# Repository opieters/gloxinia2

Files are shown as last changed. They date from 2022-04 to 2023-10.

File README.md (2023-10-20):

# gloxinia2

This is the second version of [Gloxinia](https://github.com/opieters/gloxinia), a research-focussed measurement platform that is tailored for deployment in greenhouses. Its goals are simple interconnectivity, flexbibility and cost-effectiveness.

## Architecture

The general architecture from the inital version remained, but some boards are not separate noted in place of add-on components. At it's core, the system comprises of a set of communicating nodes. Three possible options are:
- dicio: a node with serial interconnectivity, such that the system can interface with a computer. This node also features storage (16GB). This node can also send commands to other nodes in case of errors or crashes.
- sylvatica: a node with eight 16-bit ADCs
- planalta: a node with four LIAs (advanced analogue sensors)

All nodes communicate over a CAN bus and dicio nodes also have UART connection for communication computers. Plugging in a USB-C cable in the right port should suffice to connect to the system. Make sure to only plug cables to matching interfaces, since the hardware can be damaged otherwise. The interfaces are detailed in the PCB design and the interface section below. 

Note that the CAN bus requires termination. No automatic termination is implemented, so the use needs to manually terminate the CAN lines!

Each board interface also has an I2C port (not that some of the ports share the same physical interface), and analogue ports and a One Wire port. One Wire is currently not supported in the software. 

## Interfacing

Each node consists of a stack of boards. The base board with the analogue and digital processing, a botton connectivity board to interconnect different nodes and an optional top interfacing board (only for sylvatica).

### Dicio

Base board: [IF1] [IF2] [IF3] [IF4]
IF board: [Serial/USB] [] [CAN] [CAN]

### Sylvatica

Top board: [IF4] [IF5] [IF6] [IF7]
Base board: [IF1] [IF2] [IF3] [IF4]
IF board: [] [] [CAN] [CAN]

### Planalta

Base board: [IF1] [IF2] [IF3] [IF4]
IF board: [] [] [CAN] [CAN]

Note that IF1-4 are not feature-identical, IF1 supports a faster LIA (when others disabled) than IF2, 3 and 4 resp. See software implementation for details. These interfaces to no feature a 1W port.

## Software

The software consists of several parts: the embedded C code, the C++ GUI and the Python readout script. 

The embedded code is in the `firmware` folder. A separate MPLAB X project is created per hardware board (dicio, planalta and sylvatica). The code is written in C and compiled with the XC16 compiler. The code is written in a modular fashion, such that it is easy to add new features. The code is documented in the source files. Common files are included in the `lib2` folder. 

A bootloader project was also created to update the devices over CAN and UART, but this was not tested and should not yet be used in production. The UART version was slightly tested and first results were promising.

The GUI code is written in C++ using the Qt framework. A recent version of Qt 6 is necessary to build the project. Qt Designer files are included with in the `gui_qt` folder to get started with this project. 

## Enclousure

A 3D printable enclosure design is included in the `enclosure` folder, along with the STL files. The design is made in OpenSCAD.

A radiation shield was also designed for the environemental sensors, which is included in the

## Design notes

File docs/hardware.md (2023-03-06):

# Internal PIN connector

connector left

1  GND PS
3  AN1 OW1
5  AN2 OW2
7  AN3 OW3
9  AN4 OW4
11
13
15

connector right
1  VBUS   VUSBC
3  V3V3   GND
5  SDA    SCL
7  SYNC   CC1
9  D+     D-
11 CAN_C1 CAN_C2
13 RX     TX
15 nCTS   nRTS

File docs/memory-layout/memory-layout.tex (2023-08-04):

\documentclass[tikz]{standalone}

\usetikzlibrary{positioning}

\begin{document}
\begin{tikzpicture}
\begin{scope}[every node/.style={text width=4cm,align=center}]
  \node[draw] (dicio) {dicio configuration};
  \node[draw,below=0cm of dicio] (nodeconfig) {node configuration};
  \node[draw,below=0cm of nodeconfig] (data) {sample data};
\end{scope}
  
  \draw (dicio.north west) node[anchor=east] {0x0};
  \draw (nodeconfig.north west) node[anchor=east] {0x20};
  \draw (data.north west) node[anchor=east] {0x470};
  
  \draw (dicio.south east) node[anchor=west] {0x19};
  \draw (nodeconfig.south east) node[anchor=west] {0x469};
  \draw (data.south east) node[anchor=west] {0x1dacbff};
\end{tikzpicture}

\begin{tikzpicture}
\begin{scope}[every node/.style={text width=4cm,align=center}]
  \node[draw] (info) {node $n$ general info};
  \node[draw,below=0cm of info] (if1) {interface 1};
  \node[draw,below=0cm of if1] (s1-1) {sensor 1};
  \node[draw,below=0cm of s1-1] (s1-2) {sensor 2};
  \node[draw,below=0cm of s1-2] (s1-3) {sensor 3};
  \node[draw,below=0cm of s1-3] (s1-4) {sensor 4};
  \node[draw,below=0cm of s1-4] (if2) {interface 2};
  \node[draw,below=0cm of if2] (s2-1) {sensor 1};
  \node[draw,below=0cm of s2-1] (s2-2) {sensor 2};
  \node[draw,below=0cm of s2-2] (s2-3) {sensor 3};
  \node[draw,below=0cm of s2-3] (s2-4) {sensor 4};
  \node[draw,below=0cm of s2-4] (if3) {interface 3};
  \node[draw,below=0cm of if3] (if3-dots) {$\cdots$};
  \node[draw,below=0cm of if3-dots] (if4) {interface 4};
  \node[draw,below=0cm of if4] (if4-dots) {$\cdots$};
  \node[draw,below=0cm of if4-dots] (if5) {interface 5/reserved};
  \node[draw,below=0cm of if5] (if5-dots) {$\cdots$};
  \node[draw,below=0cm of if5-dots] (if6) {interface 6/reserved};
  \node[draw,below=0cm of if6] (if6-dots) {$\cdots$};
  \node[draw,below=0cm of if6-dots] (if7) {interface 7/reserved};
  \node[draw,below=0cm of if7] (if7-dots) {$\cdots$};
  \node[draw,below=0cm of if7-dots] (if8) {interface 8/reserved};
  \node[draw,below=0cm of if8] (if8-dots) {$\cdots$};
\end{scope}
  
  \draw (info.north west) node[anchor=east] {offset$_n$ + 0x0};
  \foreach \x/\y in {1/1,2/10,3/19,4/28,5/37,6/46,7/55,8/64} {
    \draw (if\x.north west) node[anchor=east] {offset$_n$ + 0x\y};
  }
  \foreach \x/\y in {1/9,2/0} {
    \draw (s\x-4.south east) node[anchor=west] {offset$_n$ + 0x\y};
  }
  \foreach \x/\y in {3/0,4/0,5/0,6/0,7/0,8/0} {
    \draw (if\x-dots.south east) node[anchor=west] {offset$_n$ + 0x\y};
  }
  
\end{tikzpicture}
\end{document}

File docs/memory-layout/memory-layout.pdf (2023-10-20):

dicio configuration

node configuration

sample data

0x0

0x20

0x470

0x19

0x469

0x1dacbff

node n general info

interface 1
sensor 1
sensor 2
sensor 3
sensor 4
interface 2
sensor 1
sensor 2
sensor 3
sensor 4
interface 3
- · ·
interface 4
- · ·
interface 5/reserved
- · ·
interface 6/reserved
- · ·
interface 7/reserved
- · ·
interface 8/reserved
- · ·

offsetn + 0x0

offsetn + 0x1

offsetn + 0x10

offsetn + 0x19

offsetn + 0x28

offsetn + 0x37

offsetn + 0x46

offsetn + 0x55

offsetn + 0x64

offsetn + 0x9

offsetn + 0x0

offsetn + 0x0

offsetn + 0x0

offsetn + 0x0

offsetn + 0x0

offsetn + 0x0

offsetn + 0x0

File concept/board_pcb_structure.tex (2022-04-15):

\documentclass[margin=2mm]{standalone}

\usepackage{tikz}
\usetikzlibrary{positioning,calc}

\begin{document}
\begin{tikzpicture}
    \draw[thick] (0,0) rectangle ++(10,10);

    \fill[green] (1,1) rectangle ++(8,8);

    \fill[red] (0.5,0) rectangle ++(9,2.5);
    \fill[gray] (0,4) rectangle ++(1.5,2);
    \fill[gray] (10,4) rectangle ++(-1.5,2);

    \foreach \x in {0,1,2,3,4} {
        \draw[ultra thick,blue] (1.75*\x+1,0) -- ++(1,0);
    }
    \draw[ultra thick,blue] (0,4.5) -- ++(0,1);
    \draw[ultra thick,blue] (10,4.5) -- ++(0,1);

\end{tikzpicture}
\end{document}

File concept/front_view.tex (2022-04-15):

\documentclass[margin=2mm]{standalone}

\usepackage{tikz}
\usetikzlibrary{positioning,calc}

\begin{document}
\begin{tikzpicture}
    \draw[thick] (0,0) rectangle ++(10,4);

    \foreach \x in {0,1,2,3,4} {
        \draw[ultra thick,blue] (1.75*\x+1,1) -- ++(1,0);
    }
    \foreach \x in {0,1,2,3,4} {
        \draw[ultra thick,blue] (1.75*\x+1,3) -- ++(1,0);
    }

    \fill[blue] (0,2) circle(2pt);
    \fill[blue] (10,2) circle(2pt);

\end{tikzpicture}
\end{document}

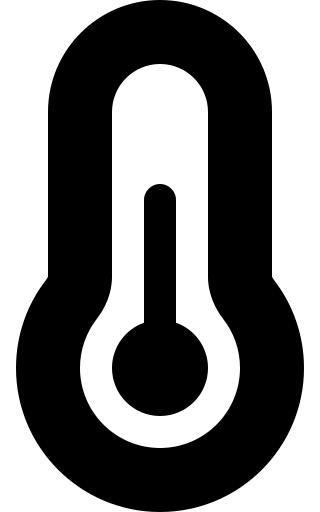
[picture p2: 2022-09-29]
gui_qt/GloxiniaConfigurator/images/temperature-rh-sensor.png

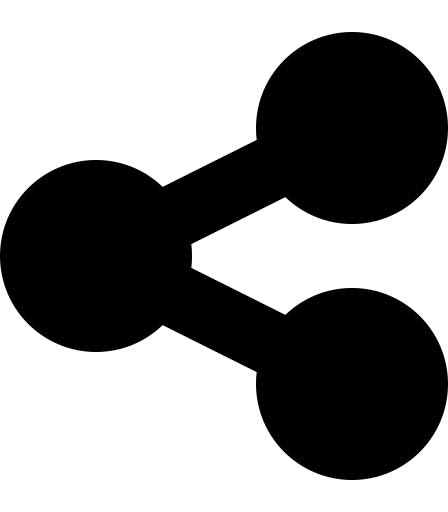
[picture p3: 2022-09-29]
gui_qt/GloxiniaConfigurator/images/node.png

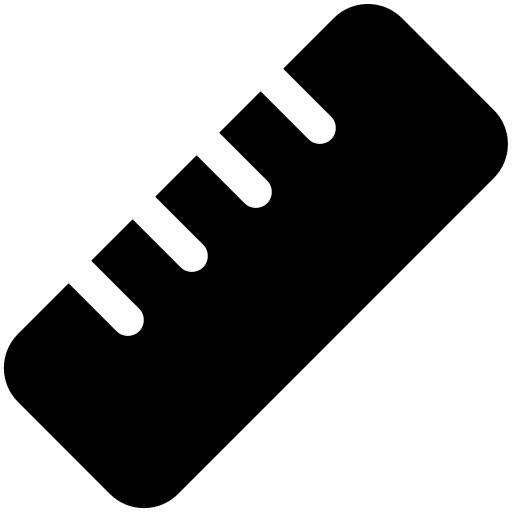
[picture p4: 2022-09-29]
gui_qt/GloxiniaConfigurator/images/general-sensor.png

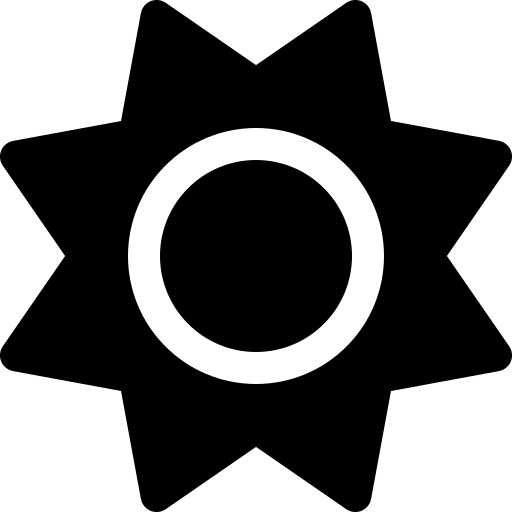
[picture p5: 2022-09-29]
gui_qt/GloxiniaConfigurator/images/light-sensor.png

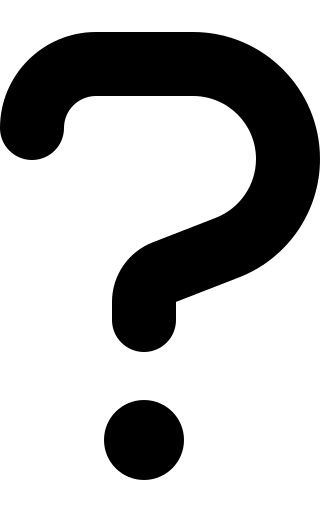
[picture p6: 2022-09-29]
gui_qt/GloxiniaConfigurator/images/unknown-sensor.png

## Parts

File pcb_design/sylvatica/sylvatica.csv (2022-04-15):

Source: | /home/opieters/PhD/gloxinia/board/sylvatica/sylvatica.sch
Date: | Tue 16 Jul 2019 10:46:27 CEST
Tool: | Eeschema 5.0.2-bee76a0~70~ubuntu18.04.1
Generator: | /home/opieters/PhD/gloxinia/board/bom-order.py
Component Count: | 106
Ref | Qnty | Value | Cmp name | Ref. Mouser | Ref. Farnell | Price
C9, | 1 | 1uF | C | 77-VJ0603A102GXJPBC
C10, | 1 | 0.01uF | C | 77-VJ0603A102GXJPBC
C11, C35, C36, C39, | 4 | C | C
C12, | 1 | 2.2uF | C | 77-VJ0603A102GXJPBC
C16, C14, C21, C19, C15, C45, C23, C24, C32, C34, C33, C37, C38, C31, C1, C2, C4, C6, C5, C7, C8, C3, | 22 | 0.1uF | C | 710-885012206071
C17, | 1 | 22uF | C | 963-TMK316BBJ226ML-T
C18, | 1 | 1uF | C | 963-TMK325B7105KD-T
C20, C13, C42, C44, | 4 | 10uF | C | 963-TMK325BJ106KM-P
C22, | 1 | 0.01uF | C | 81-GRM033C81E103KE4E
C41, C40, C26, C25, C28, C27, C30, C29, | 8 | 22nF | C | 80-C0603C223K3R
C46, C47, | 2 | 10pF | C | 603-CC603FRNPO9BN100
D1, D2, | 2 | LED | LED | 78-TLMS1000
H1, H3, H2, H4, | 4 | MountingHole | MountingHole
I0, I1, I2, I3, I4, I5, I6, I7, | 8 | AudioJack3 | AudioJack3 | 490-SJ1-3533NG
J1, | 1 | GloxiniaConnector | GloxiniaConnector
J9, | 1 | Conn_01x06_Female | Conn_01x06_Female
J14, | 1 | Conn_02x02_Odd_Even | Conn_02x02_Odd_Even
JA0, JA1, | 2 | Conn_01x03_Female | Conn_01x03_Female
JP1, | 1 | Jumper | Jumper
Q2, Q1, | 2 | Q_NMOS_GSD | Q_NMOS_GSD | 512-BSS138
R12, R14, | 2 | 0.22R | R | 667-ERJ-3RQFR22V
R13, | 1 | 1k | R | 652-CR0603-FX1001HLF
R15, R16, R9, R10, R19, | 5 | 10k | R | 284-APC0603B10K0N
R17, R18, | 2 | 750 | R | 603-RC0603FR-07750RL
R34, R33, R2, R1, R4, R3, R6, R5, | 8 | 20 | R | 71-CRCW060320R0FKEAC
R36, | 1 | 270 | R | 603-RC0603FR-07270RL
R37, | 1 | 1M | R | 603-RC0603FR-101ML
SW1, | 1 | SW_Push | SW_Push | 611-KMR621NGLFS
U5, U6, U8, U7, U1, U2, U4, U3, | 8 | PGA113 | PGA113 | 595-PGA113AIDGSR
U9, | 1 | ADS8332 | ADS8332 | 595-ADS8332IBPWR
U10, | 1 | dsPIC33EP512MC806 | dsPIC33EP512MC806 | 579-33EP512MC806IPT |  | 5
U11, | 1 | DG2034E | DG2034E | 78-DG2034EDQ-T1-GE3
U12, | 1 | LP2985-5.0 | LP2985-5.0
U13, | 1 | REF2033 | REF2033 | 595-REF2033AIDDCR
U14, | 1 | OPA320 | OPA320 | 595-OPA320AIDBVR
U15, U16, | 2 | SiP32431 | SiP32431
Y1, | 1 | Crystal_GND24 | Crystal_GND24 | 520-80-10-30B-CWNT
Total cost: | 5.00

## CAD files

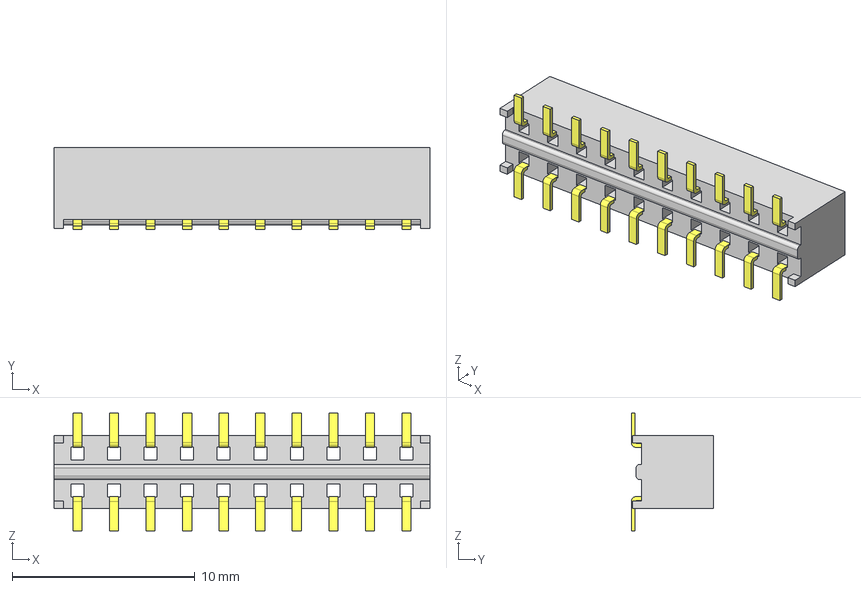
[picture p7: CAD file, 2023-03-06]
pcb_design/samtec/MMS-110-02-F-DV.stp
20.5 x 4.50 x 6.44 mm
C-63-02-10-DV
MMS-110-02-DV_socket

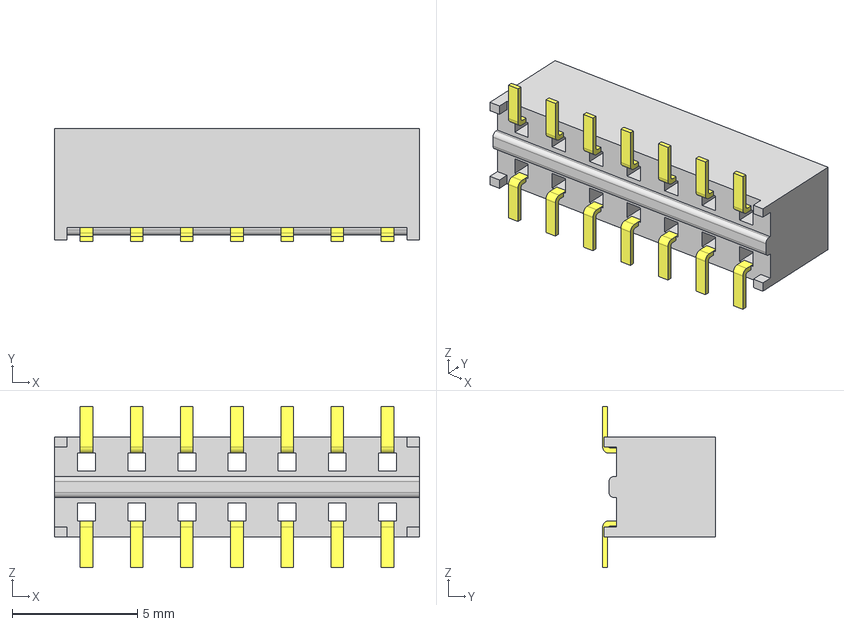
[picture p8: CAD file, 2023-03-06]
pcb_design/samtec/MMS-107-02-F-DV.stp
14.6 x 4.50 x 6.44 mm
C-63-02-07-DV
MMS-107-02-DV_socket

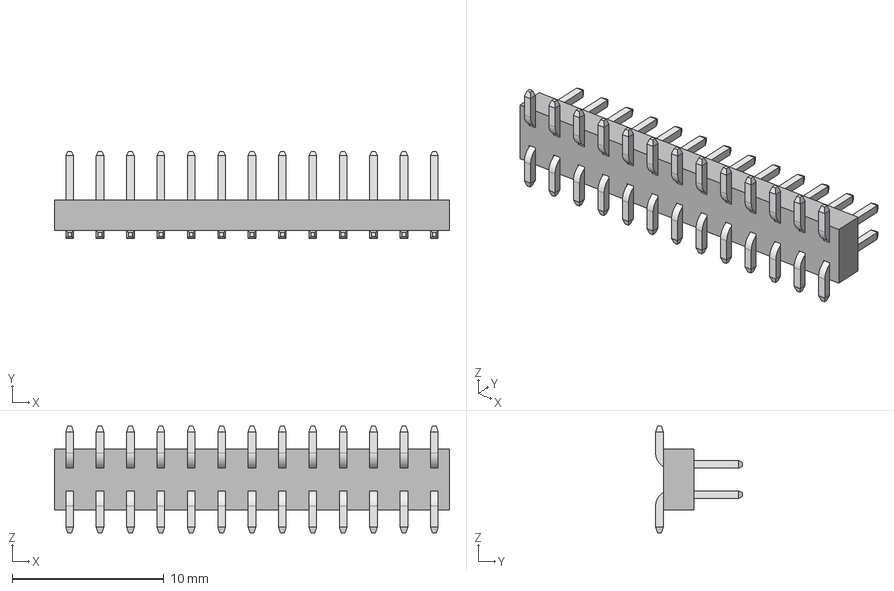
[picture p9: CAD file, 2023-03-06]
pcb_design/samtec/TMMH-113-01-T-DV.stp
26.0 x 5.71 x 7.04 mm
TMMH-113-01-T-DV-sm_pins2
TMMH-113-01-T-DV_pins1
TMMH-113-01-T-DV_body

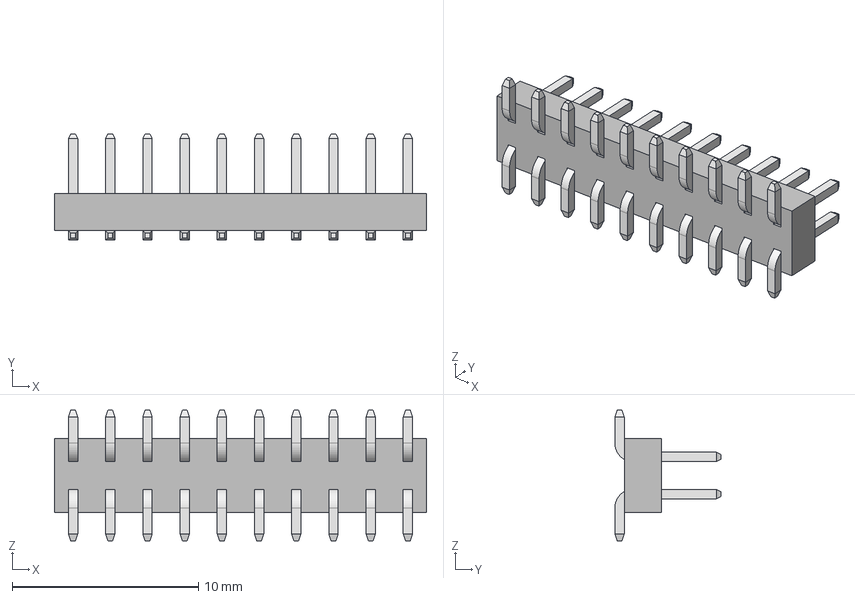
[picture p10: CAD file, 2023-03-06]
pcb_design/samtec/TMMH-110-01-T-DV.stp
20.0 x 5.71 x 7.04 mm
TMMH-110-01-T-DV-sm_pins2
TMMH-110-01-T-DV_pins1
TMMH-110-01-T-DV_body

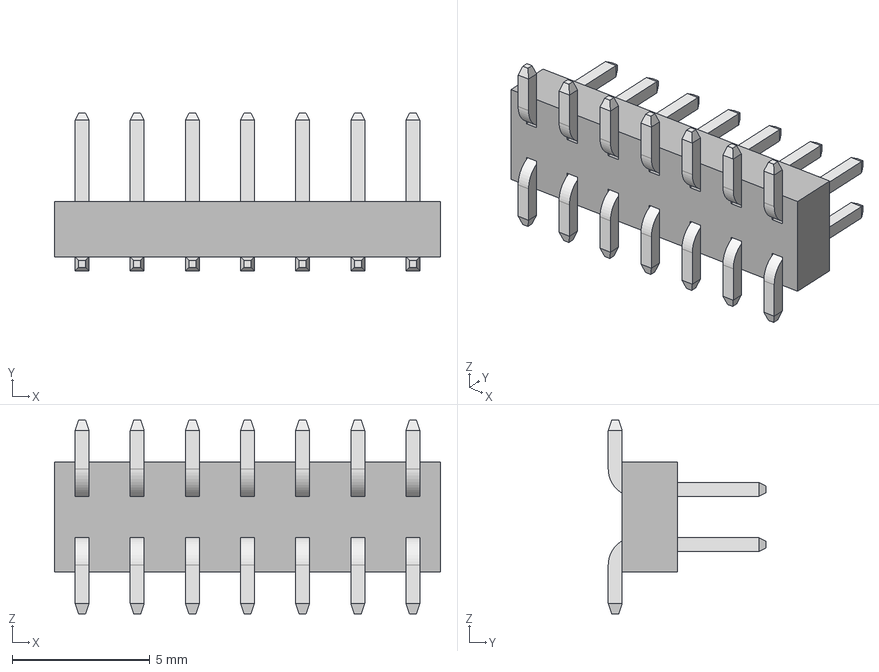
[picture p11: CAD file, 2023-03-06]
pcb_design/samtec/TMMH-107-01-T-DV.stp
14.0 x 5.71 x 7.04 mm
TMMH-107-01-T-DV-sm_pins2
TMMH-107-01-T-DV_pins1
TMMH-107-01-T-DV_body

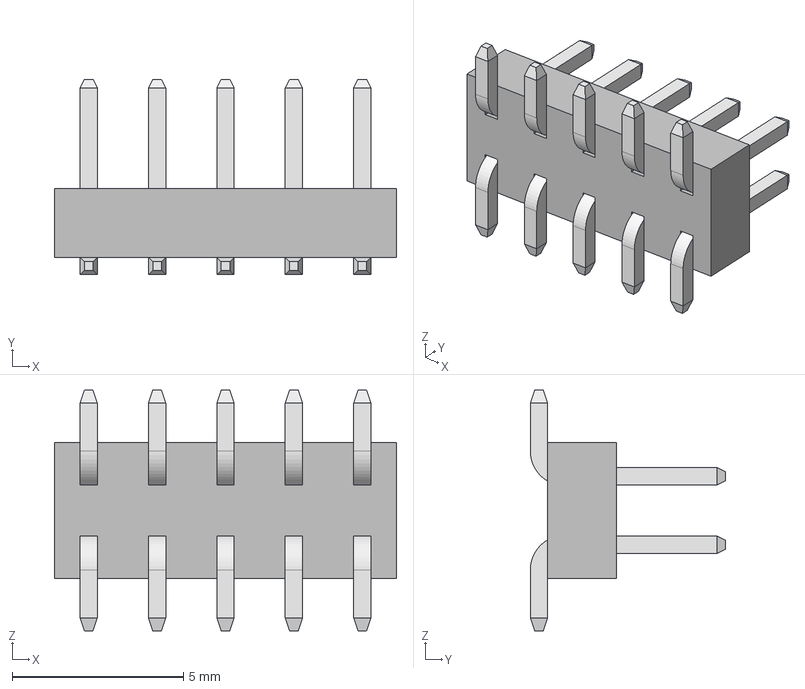
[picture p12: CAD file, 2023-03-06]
pcb_design/samtec/TMMH-105-01-T-DV.stp
10.00 x 5.71 x 7.04 mm
TMMH-105-01-T-DV-sm_pins2
TMMH-105-01-T-DV_pins1
TMMH-105-01-T-DV_body

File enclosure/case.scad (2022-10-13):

$fn=360;

module edge_primitive(){
    translate([-50,38.5])
    intersection(){
        difference(){
            translate([-1,1])
            circle(r=8);

            translate([-1,1])
            circle(r=6);
        }
        
        translate([-1,1])
        translate([8,-8])
        square([16,16],center=true);
    }

    // small piece on the side
    translate([-52.5,29.5])
    square([1.5,2]);

    // straight peice to connect top
    color("red")
    translate([-45,39.5])
    square([2,13]);

    // top piece
    translate([-45,50.5])
    square([90,2]);

    // side piece
    translate([-51.5,0])
    translate([-1,-31.5])
    square([2,65]);
}

module water_close_edge(){
    // front
    translate([0,51.5,40])
    rotate(v=[0,0,1],a=90)
    translate([0,40,0])
    rotate(v=[1,0,0],a=90)
    linear_extrude(height=84)
    polygon(points=[[-1,0], [1,0], [0.25,1.5], [-0.25, 1.5]]);

    // connector piece at the side
    translate([0,0,40])
    translate([44,46,0])
    translate([0,5.5,0])
    rotate(v=[1,0,0],a=90)
    linear_extrude(height=12)
    polygon(points=[[-1,0], [1,0], [0.25,1.5], [-0.25, 1.5]]);

    // connector piece front and side
    translate([44,51.5,40.75])
    cylinder(r1=1,r2=0.25,h=1.5,center=true);

    // arc
    translate([0,0,40])
    translate([51,39.5,0])
    rotate(v=[0,0,1],a=180)
    rotate_extrude(angle=90)
    translate([1+6,0])
    polygon(points=[[-1,0], [1,0], [0.25,1.5], [-0.25, 1.5]]);

    // small connector piece
    translate([0,0,40])
    translate([51,32.5,0])
    rotate(v=[0,0,1],a=90)
    rotate(v=[1,0,0],a=90)
    linear_extrude(height=0.5)
    polygon(points=[[-1,0], [1,0], [0.25,1.5], [-0.25, 1.5]]);

    // side piece
    translate([51.5,0,40])
    translate([0,30.5,0])
    rotate(v=[1,0,0],a=90)
    linear_extrude(height=63)
    polygon(points=[[-1,0], [1,0], [0.25,1.5], [-0.25, 1.5]]);

    // side piece connector
    translate([51.5,32.5,40.75])
    cylinder(r1=1,r2=0.25,h=1.5,center=true);
}

module base_cutout(){
    translate([-40-25,36.5])
    square([25,14]);

    translate([-46,34.5])
    translate([-2,2])
    circle(r=8);
}

/*translate([0,0,1.5])
union(){
    color("green")
    cube([76,93,3], center=true);
    color("green")
    cube([93,53,3], center=true);
}*/

//square([78,95],center=true);
//square([95,55],center=true);

// connector 
difference(){
    union(){
        // edge to raise for enclosure
        linear_extrude(height=40){
            edge_primitive();
            mirror(v=[1,0,0])
            edge_primitive();
            mirror(v=[0,1,0])
            mirror(v=[1,0,0])
            edge_primitive();
            mirror(v=[0,1,0])
            edge_primitive();
        }

        // outer shell
        linear_extrude(height=40){
        difference() {
            union(){
                square([101,105],center=true);
                square([105,101],center=true);
                translate([50.5,50.5])
                circle(r=2);
                translate([-50.5,50.5])
                circle(r=2);
                translate([50.5,-50.5])
                circle(r=2);
                translate([-50.5,-50.5])
                circle(r=2);
            }
            square([101,97],center=true);
            square([97,101],center=true);
            translate([48.5,48.5])
            circle(r=2);
            translate([-48.5,48.5])
            circle(r=2);
            translate([48.5,-48.5])
            circle(r=2);
            translate([-48.5,-48.5])
            circle(r=2);
        }
        }
    }
    
    union(){
    for(x=[-22.5, -7.5, 7.5, 22.5]){
        translate([x,53.5,7.6+1.28])
        rotate(a=90,v=[1,0,0])
        linear_extrude(height=6)
        minkowski()
        {
          circle(r=1.08);
          square([6.48,0.4],center=true);
        }
    }
    }
}

// edge for warterproof connection
water_close_edge();
mirror(v=[1,0,0])
water_close_edge();
mirror(v=[0,1,0])
water_close_edge();
mirror(v=[1,0,0])
mirror(v=[0,1,0])
water_close_edge();



// base plate
difference(){
linear_extrude(height=1){
square([105,101],center=true);
square([101,105],center=true);
translate([50.5,50.5])
circle(r=2);
translate([-50.5,50.5])
circle(r=2);
translate([50.5,-50.5])
circle(r=2);
translate([-50.5,-50.5])
circle(r=2);
}


// mounting holes of enclosure
translate([48,38,0])
cylinder(r=1.5,h=5,center=true);

translate([48,-38,0])
cylinder(r=1.5,h=5,center=true);

translate([-48,38,0])
cylinder(r=1.5,h=5,center=true);

translate([-48,-38,0])
cylinder(r=1.5,h=5,center=true);
}



// base plate
/*difference(){
    square([97,97],center=true);

    base_cutout();
    mirror(v=[0,1,0])
    base_cutout();
    mirror(v=[1,0,0])
    mirror(v=[0,1,0])
    base_cutout();
    mirror(v=[1,0,0])
    base_cutout();
}*/

// side pcb board mounting points
// moveable pcb board mounting points
for (a=[
      [32,21], [-32,21], [32,-21], [-32,-21],
      [41.5,21], [-41.5,21], [41.5,-21], [-41.5,-21],
      [33,42], [-33,42], [33,-42], [-33,-42],
      [0,-28], [0,28], [22,0], [-22,0],
]) {
translate(a)
difference(){
cylinder(h=6,r=4);
cylinder(h=7,r=2);
};
}


// mounting holes for lid
translate([48,48,0])
difference(){
    cylinder(r=4.5,h=40);
    translate([0,0,-1])
    cylinder(r=2,h=45);
}
translate([-48,48,0])
difference(){
    cylinder(r=4.5,h=40);
    translate([0,0,-1])
    cylinder(r=2,h=45);
}

translate([48,-48,0])
difference(){
    cylinder(r=4.5,h=40);
    translate([0,0,-1])
    cylinder(r=2,h=45);
}

translate([-48,-48,0])
difference(){
    cylinder(r=4.5,h=40);
    translate([0,0,-1])
    cylinder(r=2,h=45);
}

/*
for(x=[-22.5, -7.5, 7.5, 22.5]){
    color("blue")
    translate([x,53.5,7.6+1.28])
    rotate(a=90,v=[1,0,0])
    linear_extrude(height=6)
    minkowski()
    {
      circle(r=1.08);
      square([6.48,0.4],center=true);
    }
}
*/

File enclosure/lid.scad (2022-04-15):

$fn=360;

module water_close_edge(){
    translate([0,47.5,40])
    rotate(v=[0,0,1],a=90)
    translate([0,40,0])
    rotate(v=[1,0,0],a=90)
    linear_extrude(height=80)
    polygon(points=[[-1,0], [1,0], [0.25,1.5], [-0.25, 1.5]]);

    translate([0,0,40])
    translate([40,42,0])
    translate([0,5.5,0])
    rotate(v=[1,0,0],a=90)
    linear_extrude(height=12)
    polygon(points=[[-1,0], [1,0], [0.25,1.5], [-0.25, 1.5]]);

    translate([40,47.5,40.75])
    cylinder(r1=1,r2=0.25,h=1.5,center=true);

    translate([0,0,40])
    translate([47,35.5,0])
    rotate(v=[0,0,1],a=180)
    rotate_extrude(angle=90)
    translate([1+6,0])
    polygon(points=[[-1,0], [1,0], [0.25,1.5], [-0.25, 1.5]]);

    translate([0,0,40])
    translate([47,28.5,0])
    rotate(v=[0,0,1],a=90)
    rotate(v=[1,0,0],a=90)
    linear_extrude(height=.5)
    polygon(points=[[-1,0], [1,0], [0.25,1.5], [-0.25, 1.5]]);

    translate([47.5,0,40])
    translate([0,28.5,0])
    rotate(v=[1,0,0],a=90)
    linear_extrude(height=57)
    polygon(points=[[-1,0], [1,0], [0.25,1.5], [-0.25, 1.5]]);

    translate([47.5,28.5,40.75])
    cylinder(r1=1,r2=0.25,h=1.5,center=true);
}

module edge_primitive(){
    intersection(){
        difference(){
            translate([-46,34.5])
            translate([-1,1])
            circle(r=8);

            translate([-46,34.5])
            translate([-1,1])
            circle(r=6);
        }
        
        translate([-46,34.5])
        translate([-1,1])
        translate([8,-8])
        square([16,16],center=true);
    }

    translate([-48.5,27.5])
    square([1.5,2]);

    translate([-41,35.5])
    square([2,13]);

    translate([-40,46.5])
    square([80,2]);

    translate([-48.5,-28.5])
    square([2,57]);
}


difference(){
    union(){
difference(){
linear_extrude(height=1){
square([93,97],center=true);
square([97,93],center=true);
translate([46.5,46.5])
circle(r=2);
translate([-46.5,46.5])
circle(r=2);
translate([46.5,-46.5])
circle(r=2);
translate([-46.5,-46.5])
circle(r=2);
}
    translate([44,44,-3])
    cylinder(r=2,h=45);
    
    translate([-44,44,-3])
    cylinder(r=2,h=45);

    translate([44,-44,-3])
    cylinder(r=2,h=45);

    translate([-44,-44,-3])
    cylinder(r=2,h=45);
}

// edge to raise for enclosure
difference(){
    union(){
        linear_extrude(height=10){
            mirror(v=[1,0,0])
            edge_primitive();
            edge_primitive();
            mirror(v=[0,1,0])
            mirror(v=[1,0,0])
            edge_primitive();
            mirror(v=[0,1,0])
            edge_primitive();
        }
        linear_extrude(height=10)
        difference() {
            union(){
                square([93,97],center=true);
                square([97,93],center=true);
                translate([46.5,46.5])
                circle(r=2);
                translate([-46.5,46.5])
                circle(r=2);
                translate([46.5,-46.5])
                circle(r=2);
                translate([-46.5,-46.5])
                circle(r=2);
            }
            square([91,95],center=true);
            square([95,91],center=true);
            translate([45.5,45.5])
            circle(r=2);
            translate([-45.5,45.5])
            circle(r=2);
            translate([45.5,-45.5])
            circle(r=2);
            translate([-45.5,-45.5])
            circle(r=2);
        }

        // mounting holes for lid
        translate([44,44,0])
        difference(){
            cylinder(r=4.5,h=10);
            translate([0,0,-1])
            cylinder(r=2,h=45);
        }
        translate([-44,44,0])
        difference(){
            cylinder(r=4.5,h=10);
            translate([0,0,-1])
            cylinder(r=2,h=45);
        }

        translate([44,-44,0])
        difference(){
            cylinder(r=4.5,h=10);
            translate([0,0,-1])
            cylinder(r=2,h=45);
        }

        translate([-44,-44,0])
        difference(){
            cylinder(r=4.5,h=10);
            translate([0,0,-1])
            cylinder(r=2,h=45);
        }
    }
    // edge for warterproof connection
    translate([0,0,51])
    rotate(v=[0,1,0], a=180)
    union(){
        water_close_edge();
        mirror(v=[1,0,0])
        water_close_edge();
        mirror(v=[0,1,0])
        water_close_edge();
        mirror(v=[1,0,0])
        mirror(v=[0,1,0])
        water_close_edge();
    }
}
}
    translate([44,44,0])
    translate([0,0,-5])
    cylinder(r1=4.5,r2=2,h=10);

    translate([44,-44,0])
    translate([0,0,-5])
    cylinder(r1=4.5,r2=2,h=10);

    translate([-44,44,0])
    translate([0,0,-5])
    cylinder(r1=4.5,r2=2,h=10);

    translate([-44,-44,0])
    translate([0,0,-5])
    cylinder(r1=4.5,r2=2,h=10);
}


    
// mounting holes for lid

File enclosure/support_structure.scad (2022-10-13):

$fn=360;

module connection_grid(){
    for(p=[
        //[[32,21],[-32,21]],
        //[[-32,21],[32,21]],
        //[[32,-21],[-32,-21]],
        //[[-32,-21],[32,-21]],
        [[32,21],[32,-21]],
        [[32,-21],[32,21]],
        [[-32,21],[-32,-21]],
        [[-32,-21],[-32,21]],

        [[33,42],[32,21]],
        [[-33,42],[-32,21]],
        [[32,21],[33,42],],
        [[-32,21],[-33,42],],

        [[33,-42],[32,-21]],
        [[-33,-42],[-32,-21]],
        [[32,-21],[33,-42],],
        [[-32,-21],[-33,-42],],

        [[32,21],[0,28]],
        [[0,28],[32,21]],
        [[-32,21],[0,28]],
        [[0,28],[-32,21]],

        [[32,-21],[0,-28]],
        [[0,-28],[32,-21]],
        [[-32,-21],[0,-28]],
        [[0,-28],[-32,-21]],
        
        [[0,-28],[-33,-42]],
        [[0,-28],[33,-42]],
        [[-33,-42],[0,-28]],
        [[33,-42],[0,-28]],
        
        [[0,28],[-33,42]],
        [[0,28],[33,42]],
        [[-33,42],[0,28]],
        [[33,42],[0,28]],
        
        [[22,0], [32,21]],
        [[22,0], [32,-21]],
        [[32,21], [22,0]],
        [[32,-21], [22,0]],
        
        [[-22,0], [-32,21]],
        [[-22,0], [-32,-21]],
        [[-32,21], [-22,0]],
        [[-32,-21], [-22,0]],
        
        [[-22,0], [0,28]],
        [[22,0], [0,28]],
        [[-22,0], [0,-28]],
        [[22,0], [0,-28]],
        
        [[0,28], [-22,0]],
        [[0,28], [22,0]],
        [[0,-28], [-22,0]],
        [[0,-28], [22,0]],
    ]){
    x1 = p[0];
    x2 = p[1];
    
    xv = x1-x2;
    xc = (x1+x2)/2;
        echo(xv);

    xv_angle = xv[1] > 0 ? acos(xv*[1,0] / norm(xv)) : -acos(xv*[1,0] / norm(xv));

    //tilt_angle = 10;
    //tilt = norm(xv)/2*sin(tilt_angle);
    tilt = 7.5;
    tilt_angle = asin(2*tilt / norm(xv));

    translate([0,0,tilt])
    translate([xc[0],xc[1],0])
    translate([0,0,0.5*tilt])
    rotate(a=xv_angle,v=[0,0,1])
    rotate(a=tilt_angle,v=[0,1,0])
    translate([-norm(xv)/2, 0, 0])
    rotate(v=[0,1,0], a=90)
    linear_extrude(norm(xv))
    square([1.5,1.5], center=true);
}
}

module support_grid(){
        for(p=[
            [[32,21],[32,-21]],
            [[-32,-21],[-32,21]],

            [[33,42],[32,21]],
            [[-33,42],[-32,21]],

            [[-33,-42],[-32,-21]],
            [[32,-21],[33,-42],],
        
            [[0,28],[32,21]],
            [[0,28],[-32,21]],

            [[32,-21],[0,-28]],
            [[-32,-21],[0,-28]],
            
            [[0,-28],[-33,-42]],
            [[0,-28],[33,-42]],
            
            [[0,28],[-33,42]],
            [[0,28],[33,42]],
            
            [[22,0], [32,21]],
            [[22,0], [32,-21]],
            
            [[-22,0], [-32,21]],
            [[-22,0], [-32,-21]],
            
            [[-22,0], [0,-28]],
            [[22,0], [0,-28]],
            
            [[0,28], [-22,0]],
            [[0,28], [22,0]],
            
            [[-33,-42],[33,-42]],
            [[-33,42],[33,42]],
        ]){
        x1 = p[0];
        x2 = p[1];
        
        xv = x1-x2;
        xc = (x1+x2)/2;

        xv_angle = xv[1] > 0 ? acos(xv*[1,0] / norm(xv)) : -acos(xv*[1,0] / norm(xv));

        //translate([0,0,tilt])
        translate([xc[0],xc[1],0])
        translate([0,0,0.25])
        rotate(a=xv_angle,v=[0,0,1])
        //rotate(a=tilt_angle,v=[0,1,0])
        translate([-norm(xv)/2, 0, 0])
        rotate(v=[0,1,0], a=90)
        linear_extrude(norm(xv))
        square([0.5,1.5], center=true);
    }
}


difference(){
    union(){
        for (a=[
              [32,21], [-32,21], 
              [32,-21], [-32,-21],
              //[33,42], [-33,42], 
              //[33,-42], [-33,-42],
              //[0,-28], [0,28], 
              [22,0], [-22,0],
        ]) {
            translate(a)
            cylinder(h=20,r=3.5);
        }
        
        for (a=[
              //[32,21], [-32,21], 
              //[32,-21], [-32,-21],
              [33,42], [-33,42], 
              [33,-42], [-33,-42],
              [0,-28], [0,28], 
        ]) {
            translate(a)
            cylinder(h=25,r=3.5);
        }
        
        connection_grid();
        support_grid();
    }

    for (a=[
          //[32,21], [-32,21], [32,-21], [-32,-21],
          [32,21], [-32,21], 
          [32,-21], [-32,-21],
          [33,42], [-33,42], 
          [33,-42], [-33,-42],
          [0,-28], [0,28], 
          [22,0], [-22,0],
    ]) {
        translate([0,0,-1])
        translate(a)
        cylinder(h=35,r=2);
    }
}

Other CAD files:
radiation_shield/radiation_shield.scad

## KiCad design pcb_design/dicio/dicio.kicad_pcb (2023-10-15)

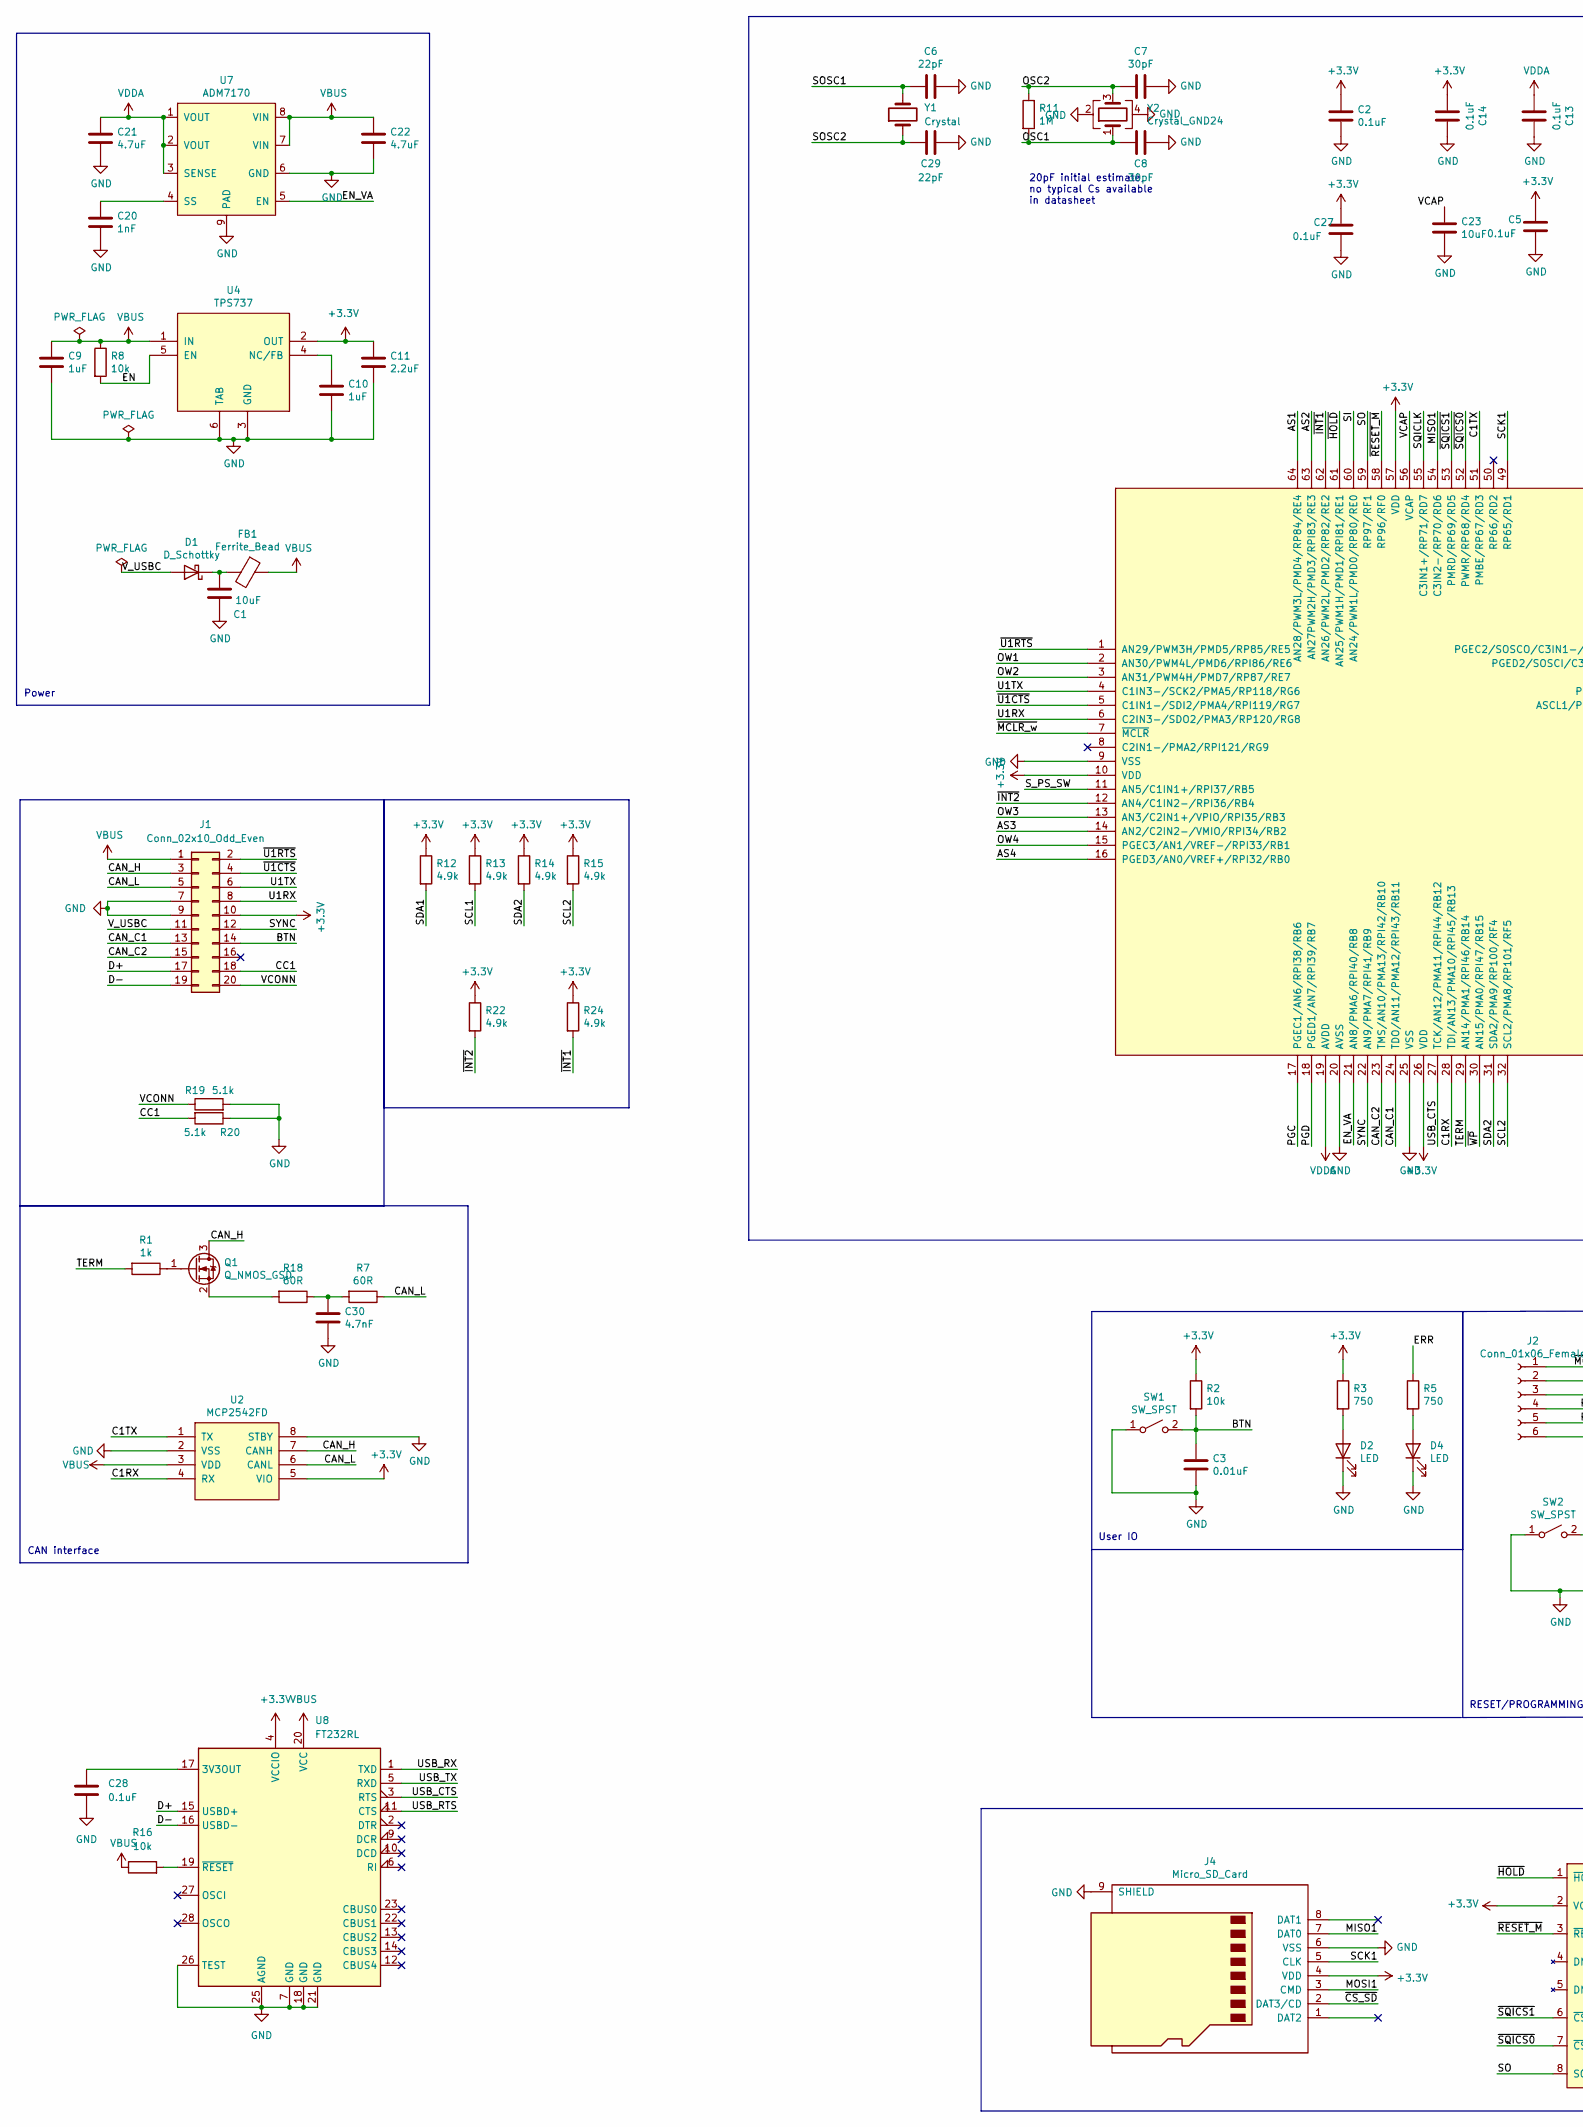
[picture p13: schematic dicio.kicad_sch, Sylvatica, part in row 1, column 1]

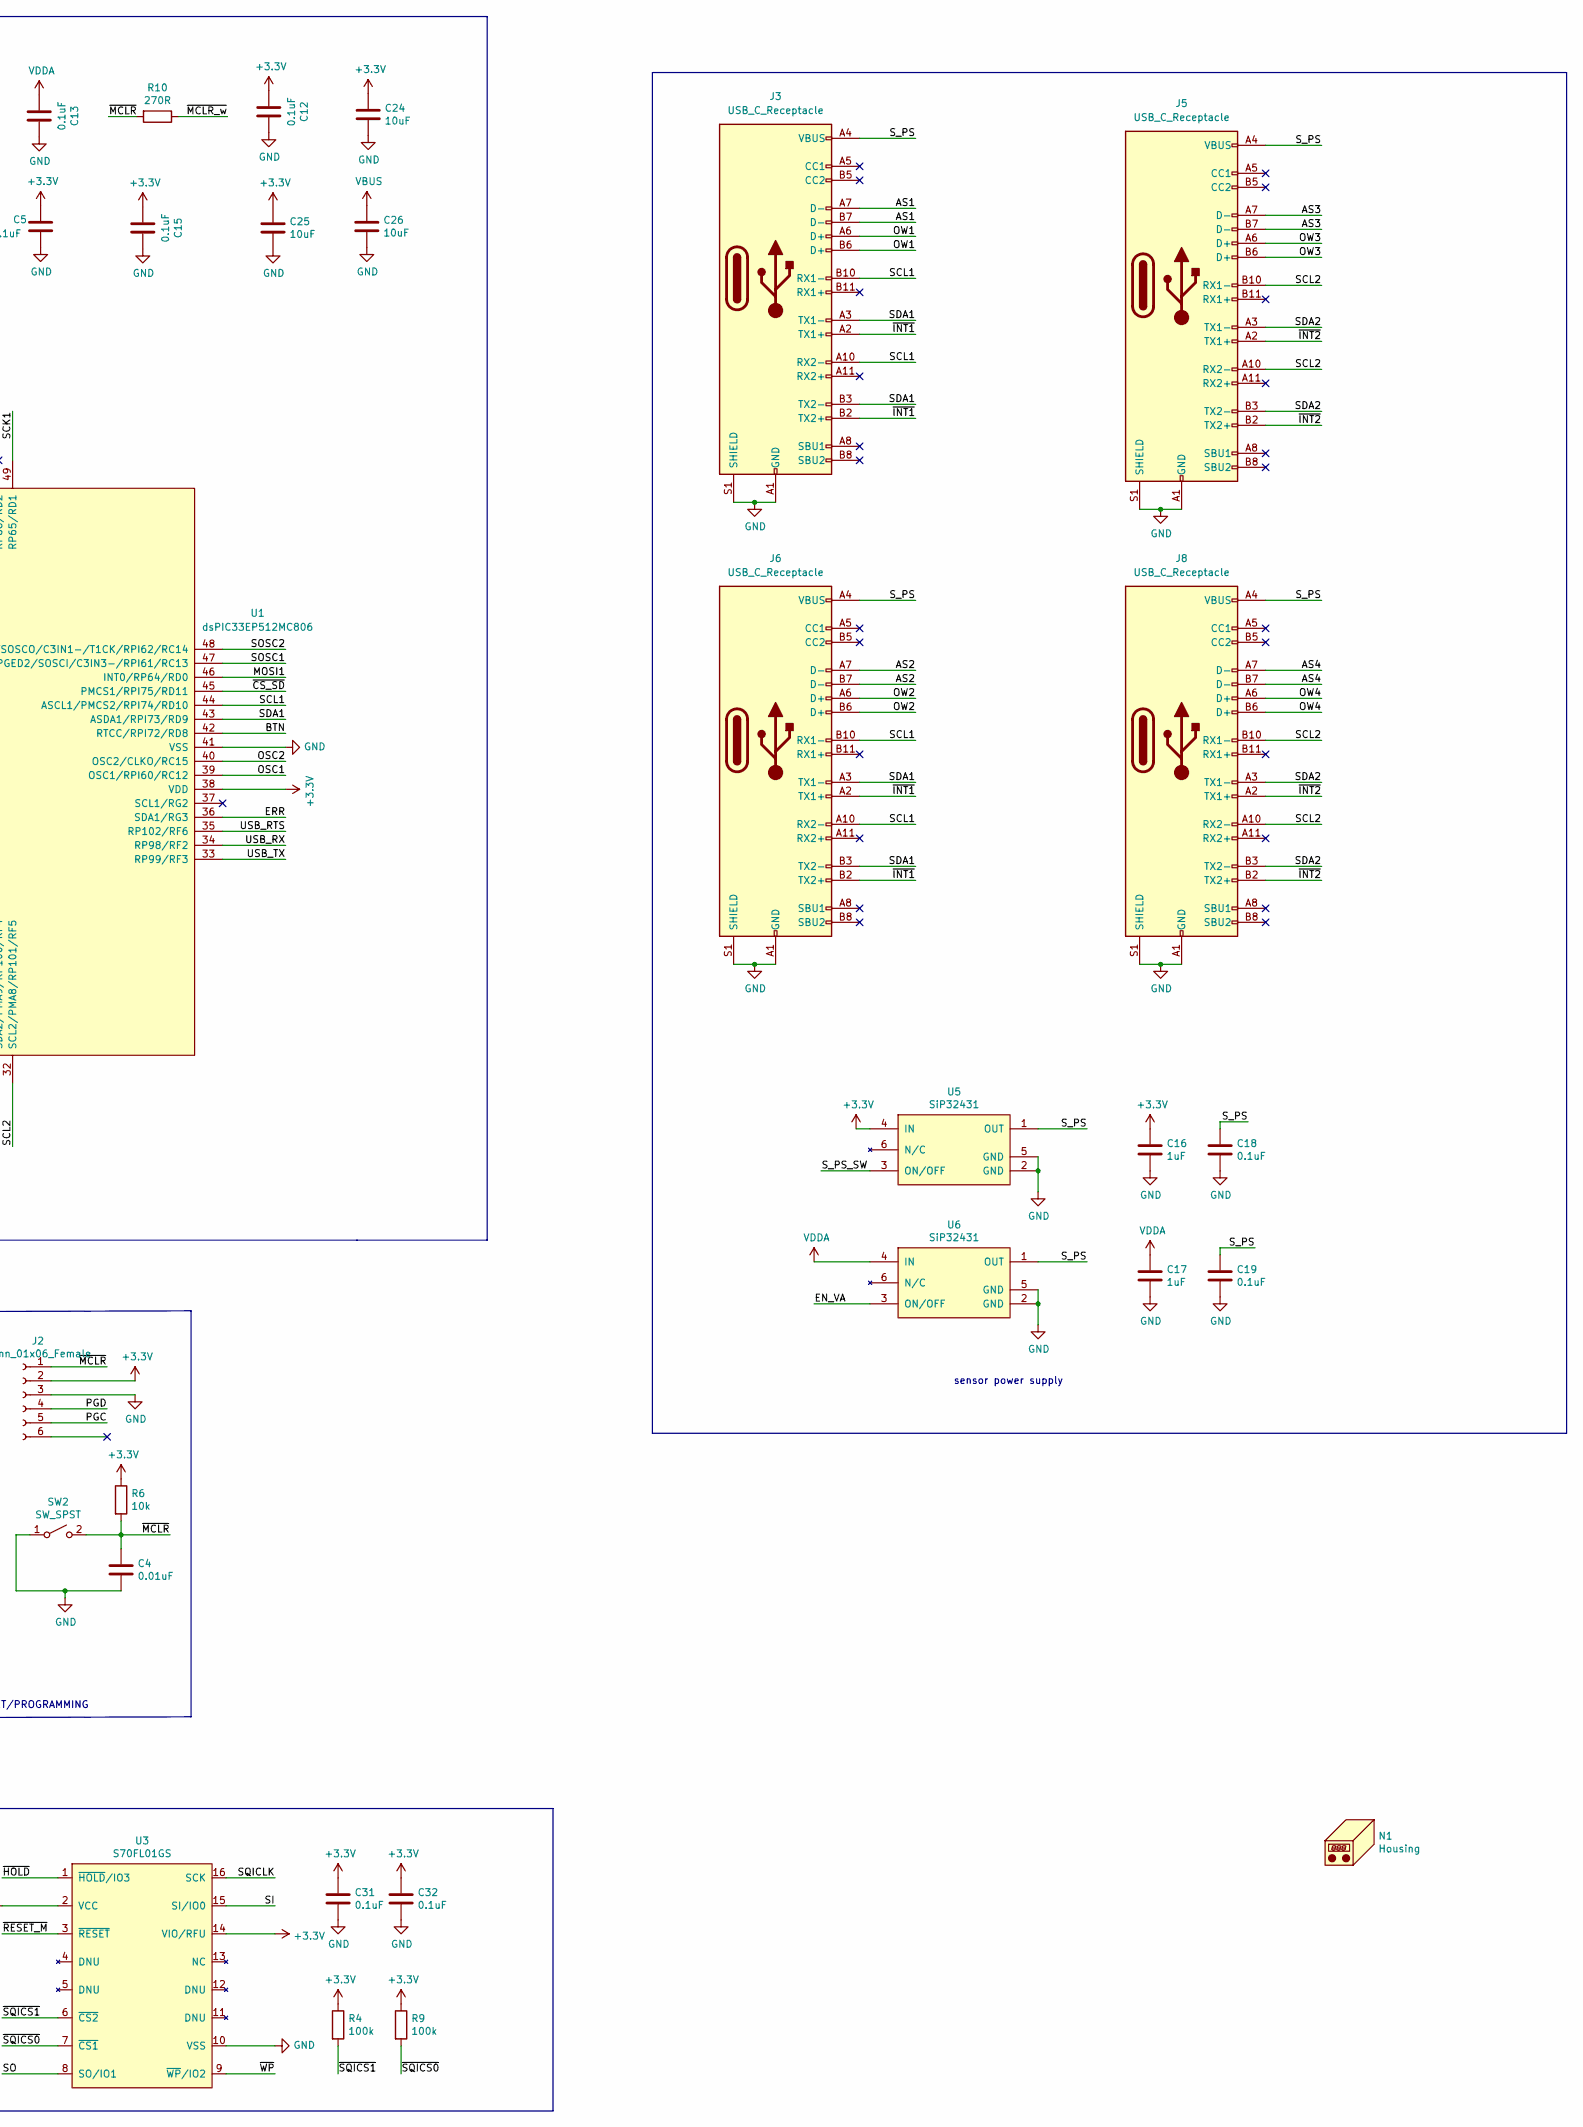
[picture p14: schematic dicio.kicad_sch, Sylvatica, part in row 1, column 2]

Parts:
C1, C24, C25, C26: 10uF; C_1210_3225Metric; Mouser 963-TMK325BJ106KM-P
C2, C5, C12, C13, C14, C15, C27: 0.1uF; C_0603_1608Metric; Mouser 710-885012206071
C3, C4: 0.01uF; C_0603_1608Metric; Mouser 710-885012206065
C6, C29: 22pF; C_0603_1608Metric; Mouser 80-C0603C220J3HACTU
C7, C8: 30pF; C_0603_1608Metric; Mouser 80-C0603C300G1HACTU
C9, C10: 1uF; C_0603_1608Metric; Mouser 963-TMK325B7105KD-T
C11: 2.2uF; C_1206_3216Metric; Mouser 791-1206X225K250CT
C16, C17: 1uF; C_0603_1608Metric
C18, C19, C28, C31, C32: 0.1uF; C_0603_1608Metric
C20: 1nF; C_0603_1608Metric
C21, C22: 4.7uF; C_1206_3216Metric; Mouser 80-C1206C475K4PAC
C23: 10uF; C_1210_3225Metric
C30: 4.7nF; C_0603_1608Metric
D1: D_Schottky; D_SMB; Mouser 621-B340LB-F
D2, D4: LED; LED_0603_1608Metric; Mouser 78-TLMS1000
FB1: Ferrite_Bead; L_0805_2012Metric; Mouser 875-MI0805K400R-10
J1: Conn_02x10_Odd_Even; SAMTEC_TMMH-110-01-T-DV
J2: Conn_01x06_Female; PinSocket_1x06_P2.54mm_Vertical
J3, J5, J6, J8: USB_C_Receptacle; USB_C_Receptacle_Amphenol_12401861XX12A; Mouser 523-124018612112A
J4: Micro_SD_Card; microSD_HC_Wuerth_693072010801
N1: Housing; Enclosure-Gloxinia4; Mouser 546-1554LA2GYCL
Q1: Q_NMOS_GSD; SOT-23; Mouser 771-PMV20XNER
R1: 1k; R_0603_1608Metric
R2, R6, R8: 10k; R_0603_1608Metric; Mouser 284-APC0603B10K0N
R3, R5: 750; R_0603_1608Metric; Mouser 603-RC0603FR-07750RL
R4, R9: 100k; R_0603_1608Metric
R7, R18: 60R; R_0603_1608Metric; Mouser 594-5063JD120R0F
R10: 270R; R_0603_1608Metric; Mouser 603-RC0603FR-07270RL
R11: 1M; R_0603_1608Metric
R12, R13, R14, R15, R22, R24: 4.9k; R_0603_1608Metric; Mouser 603-RC0603FR-0724K9L
R16: 10k; R_0603_1608Metric
R19, R20: 5.1k; R_0603_1608Metric; Mouser 603-AC0603FR-135K1L
SW1, SW2: SW_SPST; SW_Push_1P1T_NO_CK_KMR2; Mouser 611-KMR621NGLFS
U1: dsPIC33EP512MC806; TQFP-64_10x10mm_P0.5mm
U2: MCP2542FD; SOIC-8_3.9x4.9mm_P1.27mm; Mouser 579-MCP2542FDT-E/SN
U3: S70FL01GS; SOIC-16_25.75x18.75mm_P2.5mm
U4: TPS737; SOT-223-6; Mouser 595-TPS73733DCQR
U5, U6: SiP32431; SOT-363_SC-70-6
U7: ADM7170; LFCSP-8-1EP_3x3mm_P0.5mm_EP1.45x1.74mm
U8: FT232RL; SSOP-28_5.3x10.2mm_P0.65mm
Y1: Crystal; Crystal_SMD_3215-2Pin_3.2x1.5mm; Mouser 520-.327-9-34QCNT
Y2: Crystal_GND24; Crystal_SMD_Abracon_ABM3B-4Pin_5.0x3.2mm; Mouser 520-80-10-30B-CWNT

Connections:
+3.3V: C2.1, C5.1, C11.1, C12.2, C14.2, C15.1, C16.1, C24.1, C25.1, C27.1, C31.1, C32.1, J1.10, J2.2, J4.4 (VDD), R2.1, R3.1, R4.1, R6.1, R9.1, R12.1, R13.1, R14.1, R15.1, R22.1, R24.1, U1.10 (VDD), U1.26 (VDD), U1.38 (VDD), U1.57 (VDD), U2.5 (VIO), U3.2 (VCC), U3.14 (VIO/RFU), U4.2 (OUT), U5.4 (IN), U8.4 (VCCIO)
/AS1: J3.A7 (D-), J3.B7 (D-), U1.64 (AN28/PWM3L/PMD4/RP84/RE4)
/AS2: J6.A7 (D-), J6.B7 (D-), U1.63 (AN27PWM2H/PMD3/RPI83/RE3)
/AS3: J5.A7 (D-), J5.B7 (D-), U1.14 (AN2/C2IN2-/VMIO/RPI34/RB2)
/AS4: J8.A7 (D-), J8.B7 (D-), U1.16 (PGED3/AN0/VREF+/RPI32/RB0)
/BTN: C3.1, J1.14, R2.2, SW1.2 (B), U1.42 (RTCC/RPI72/RD8)
/C1RX: U1.28 (TDI/AN13/PMA10/RPI45/RB13), U2.4 (RX)
/C1TX: U1.51 (PMBE/RP67/RD3), U2.1 (TX)
/CAN_C1: J1.13, U1.24 (TDO/AN11/PMA12/RPI43/RB11)
/CAN_C2: J1.15, U1.23 (TMS/AN10/PMA13/RPI42/RB10)
/CAN_H: J1.3, Q1.3 (D), U2.7 (CANH)
/CAN_L: J1.5, R7.1, U2.6 (CANL)
/CC1: J1.18, R20.2
/D+: J1.17, U8.15 (USBD+)
/D-: J1.19, U8.16 (USBD-)
/EN: R8.2, U4.5 (EN)
/EN_VA: U1.21 (AN8/PMA6/RPI40/RB8), U6.3 (ON/OFF), U7.5 (EN)
/ERR: R5.1, U1.36 (SDA1/RG3)
/MISO1: J4.7 (DAT0), U1.54 (C3IN2-/RP70/RD6)
/MOSI1: J4.3 (CMD), U1.46 (INT0/RP64/RD0)
/OSC1: C8.2, R11.2, U1.39 (OSC1/RPI60/RC12), Y2.1
/OSC2: C7.2, R11.1, U1.40 (OSC2/CLKO/RC15), Y2.3
/OW1: J3.A6 (D+), J3.B6 (D+), U1.2 (AN30/PWM4L/PMD6/RPI86/RE6)
/OW2: J6.A6 (D+), J6.B6 (D+), U1.3 (AN31/PWM4H/PMD7/RP87/RE7)
/OW3: J5.A6 (D+), J5.B6 (D+), U1.13 (AN3/C2IN1+/VPIO/RPI35/RB3)
/OW4: J8.A6 (D+), J8.B6 (D+), U1.15 (PGEC3/AN1/VREF-/RPI33/RB1)
/PGC: J2.5, U1.17 (PGEC1/AN6/RPI38/RB6)
/PGD: J2.4, U1.18 (PGED1/AN7/RPI39/RB7)
/SCK1: J4.5 (CLK), U1.49 (RP65/RD1)
/SCL1: J3.A10 (RX2-), J3.B10 (RX1-), J6.A10 (RX2-), J6.B10 (RX1-), R13.2, U1.44 (ASCL1/PMCS2/RPI74/RD10)
/SCL2: J5.A10 (RX2-), J5.B10 (RX1-), J8.A10 (RX2-), J8.B10 (RX1-), R15.2, U1.32 (SCL2/PMA8/RP101/RF5)
/SDA1: J3.A3 (TX1-), J3.B3 (TX2-), J6.A3 (TX1-), J6.B3 (TX2-), R12.2, U1.43 (ASDA1/RPI73/RD9)
/SDA2: J5.A3 (TX1-), J5.B3 (TX2-), J8.A3 (TX1-), J8.B3 (TX2-), R14.2, U1.31 (SDA2/PMA9/RP100/RF4)
/SI: U1.60 (AN24/PWM1L/PMD0/RP80/RE0), U3.15 (SI/IO0)
/SO: U1.59 (RP97/RF1), U3.8 (SO/IO1)
/SOSC1: C6.2, U1.47 (PGED2/SOSCI/C3IN3-/RPI61/RC13), Y1.2
/SOSC2: C29.2, U1.48 (PGEC2/SOSCO/C3IN1-/T1CK/RPI62/RC14), Y1.1
/SQICLK: U1.55 (C3IN1+/RP71/RD7), U3.16 (SCK)
/SYNC: J1.12, U1.22 (AN9/PMA7/RPI41/RB9)
/S_PS: C18.1, C19.1, J3.A4 (VBUS), J3.A9 (VBUS), J3.B4 (VBUS), J3.B9 (VBUS), J5.A4 (VBUS), J5.A9 (VBUS), J5.B4 (VBUS), J5.B9 (VBUS), J6.A4 (VBUS), J6.A9 (VBUS), J6.B4 (VBUS), J6.B9 (VBUS), J8.A4 (VBUS), J8.A9 (VBUS), J8.B4 (VBUS), J8.B9 (VBUS), U5.1 (OUT), U6.1 (OUT)
/S_PS_SW: U1.11 (AN5/C1IN1+/RPI37/RB5), U5.3 (ON/OFF)
/TERM: R1.2, U1.29 (AN14/PMA1/RPI46/RB14)
/U1RX: J1.8, U1.6 (C2IN3-/SDO2/PMA3/RP120/RG8)
/U1TX: J1.6, U1.4 (C1IN3-/SCK2/PMA5/RP118/RG6)
/USB_CTS: U1.27 (TCK/AN12/PMA11/RPI44/RB12), U8.3 (RTS)
/USB_RTS: U1.35 (RP102/RF6), U8.11 (CTS)
/USB_RX: U1.34 (RP98/RF2), U8.1 (TXD)
/USB_TX: U1.33 (RP99/RF3), U8.5 (RXD)
/VCAP: C23.1, U1.56 (VCAP)
/VCONN: J1.20, R19.1
/V_USBC: D1.2 (A), J1.11
/~CS_SD: J4.2 (DAT3/CD), U1.45 (PMCS1/RPI75/RD11)
/~HOLD: U1.61 (AN25/PWM1H/PMD1/RPI81/RE1), U3.1 (~HOLD/IO3)
/~INT1: J3.A2 (TX1+), J3.B2 (TX2+), J6.A2 (TX1+), J6.B2 (TX2+), R24.2, U1.62 (AN26/PWM2L/PMD2/RP82/RE2)
/~INT2: J5.A2 (TX1+), J5.B2 (TX2+), J8.A2 (TX1+), J8.B2 (TX2+), R22.2, U1.12 (AN4/C1IN2-/RPI36/RB4)
/~MCLR_w: R10.1, U1.7 (~MCLR)
/~MCLR: C4.1, J2.1, R6.2, R10.2, SW2.2 (B)
/~RESET_M: U1.58 (RP96/RF0), U3.3 (~RESET)
/~SQICS0: R9.2, U1.52 (PWMR/RP68/RD4), U3.7 (~CS1)
/~SQICS1: R4.2, U1.53 (PMRD/RP69/RD5), U3.6 (~CS2)
/~U1CTS: J1.4, U1.5 (C1IN1-/SDI2/PMA4/RPI119/RG7)
/~U1RTS: J1.2, U1.1 (AN29/PWM3H/PMD5/RP85/RE5)
/~WP: U1.30 (AN15/PMA0/RPI47/RB15), U3.9 (~WP/IO2)
GND: C1.2, C2.2, C3.2, C4.2, C5.2, C6.1, C7.1, C8.1, C9.2, C10.2, C11.2, C12.1, C13.1, C14.1, C15.2, C16.2, C17.2, C18.2, C19.2, C20.2, C21.2, C22.2, C23.2, C24.2, C25.2, C26.2, C27.2, C28.2, C29.1, C30.2, C31.2, C32.2, D2.1 (K), D4.1 (K), J1.7, J1.9, J2.3, J3.A1 (GND), J3.A12 (GND), J3.B1 (GND), J3.B12 (GND), J3.S1 (SHIELD), J4.6 (VSS), J4.9 (SHIELD), J5.A1 (GND), J5.A12 (GND), J5.B1 (GND), J5.B12 (GND), J5.S1 (SHIELD), J6.A1 (GND), J6.A12 (GND), J6.B1 (GND), J6.B12 (GND), J6.S1 (SHIELD), J8.A1 (GND), J8.A12 (GND), J8.B1 (GND), J8.B12 (GND), J8.S1 (SHIELD), R19.2, R20.1, SW1.1 (A), SW2.1 (A), U1.9 (VSS), U1.20 (AVSS), U1.25 (VSS), U1.41 (VSS), U2.2 (VSS), U2.8 (STBY), U3.10 (VSS), U4.3 (GND), U4.6 (TAB), U5.2 (GND), U5.5 (GND), U6.2 (GND), U6.5 (GND), U7.6 (GND), U7.9 (PAD), U8.7 (GND), U8.18 (GND), U8.21 (GND), U8.25 (AGND), U8.26 (TEST), Y2.2, Y2.4
unnamed: C1.1, D1.1 (K), FB1.2
unnamed: C10.1, U4.4 (NC/FB)
unnamed: C20.1, U7.4 (SS)
unnamed: C28.1, U8.17 (3V3OUT)
unnamed: C30.1, R7.2, R18.1
unnamed: D2.2 (A), R3.2
unnamed: D4.2 (A), R5.2
unnamed: Q1.1 (G), R1.1
unnamed: Q1.2 (S), R18.2
unnamed: R16.2, U8.19 (~RESET)
VBUS: C9.1, C22.1, C26.1, FB1.1, J1.1, R8.1, R16.1, U2.3 (VDD), U4.1 (IN), U7.7 (VIN), U7.8 (VIN), U8.20 (VCC)
VDDA: C13.2, C17.1, C21.1, U1.19 (AVDD), U6.4 (IN), U7.1 (VOUT), U7.2 (VOUT), U7.3 (SENSE)

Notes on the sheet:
sensor power supply
20pF initial estimate, no typical Cs available in datasheet
RESET/PROGRAMMING
CAN interface
User IO
Power

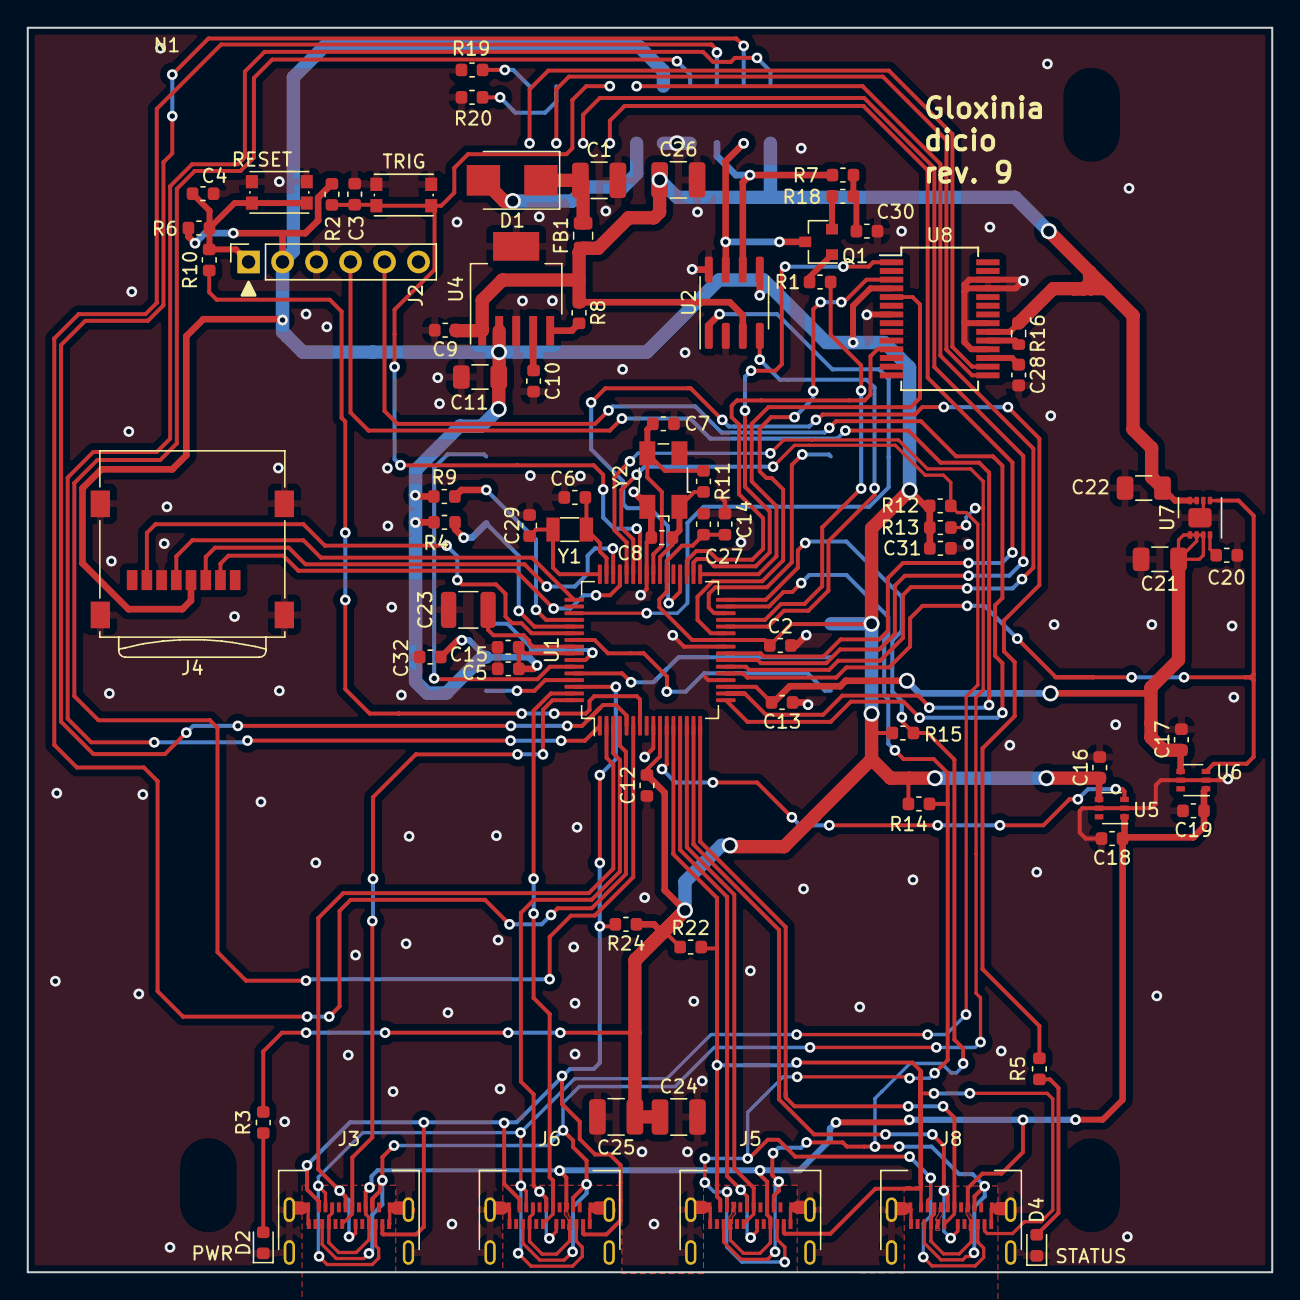
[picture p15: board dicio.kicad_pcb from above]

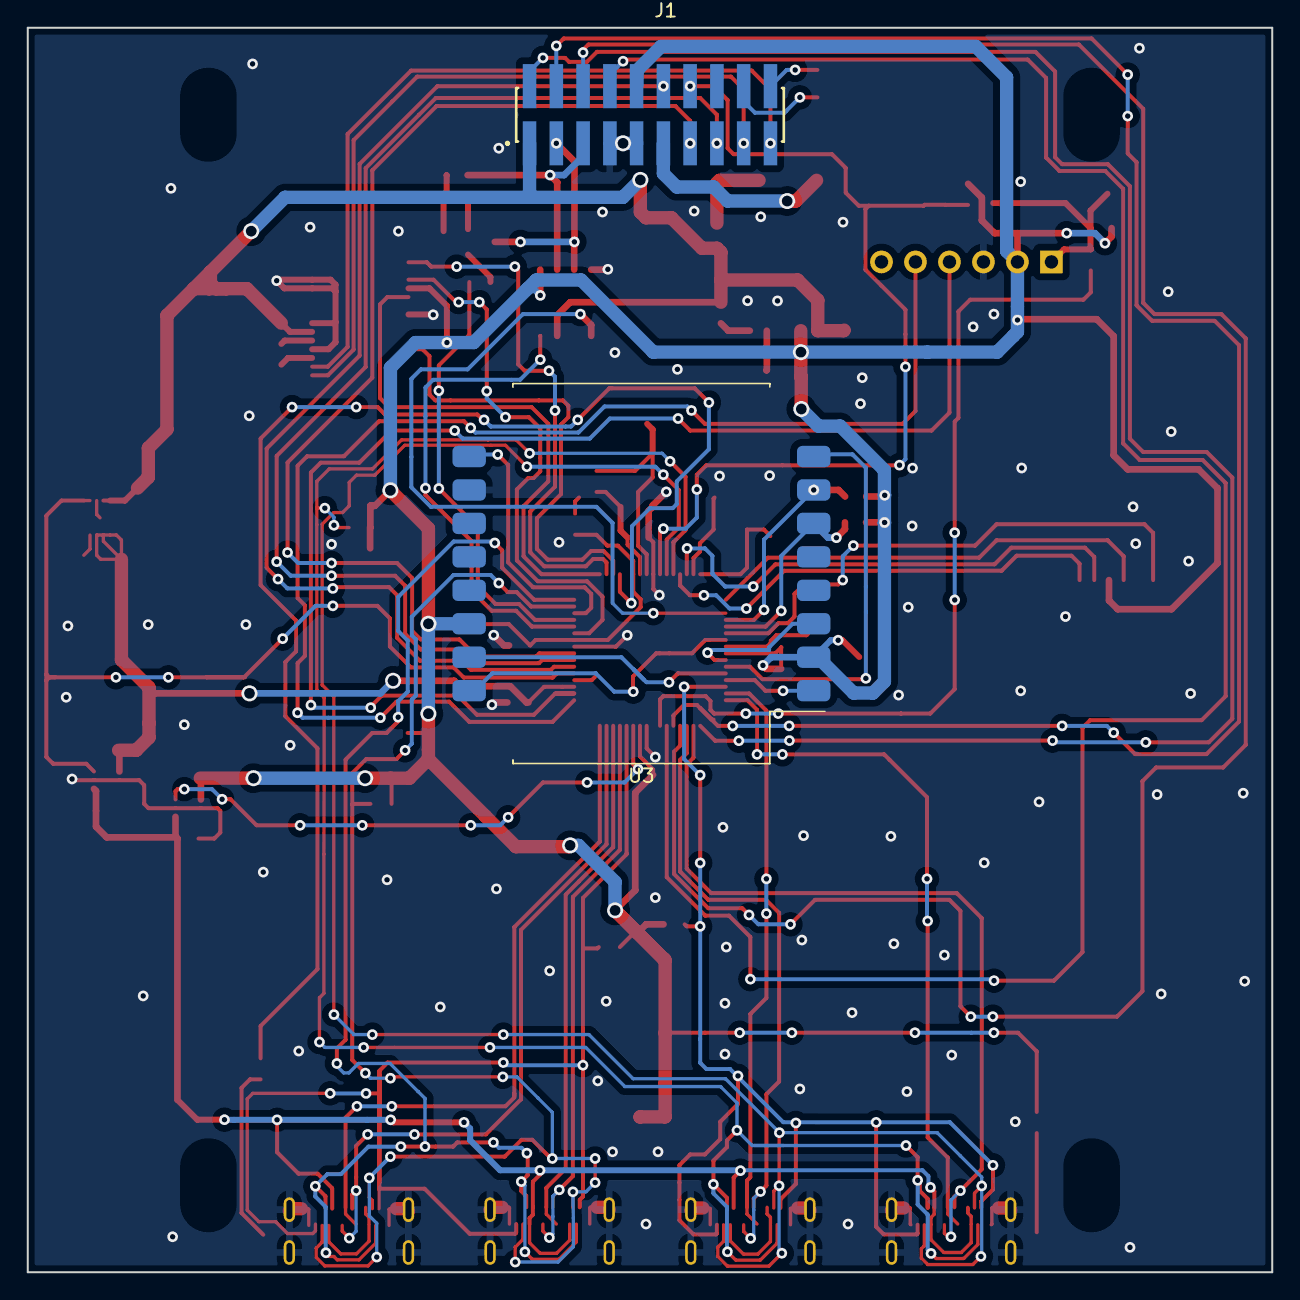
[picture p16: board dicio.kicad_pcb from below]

Board: 2 copper layers, 93.0 x 93.0 mm, 78 parts (2 on the bottom side), 76 nets.

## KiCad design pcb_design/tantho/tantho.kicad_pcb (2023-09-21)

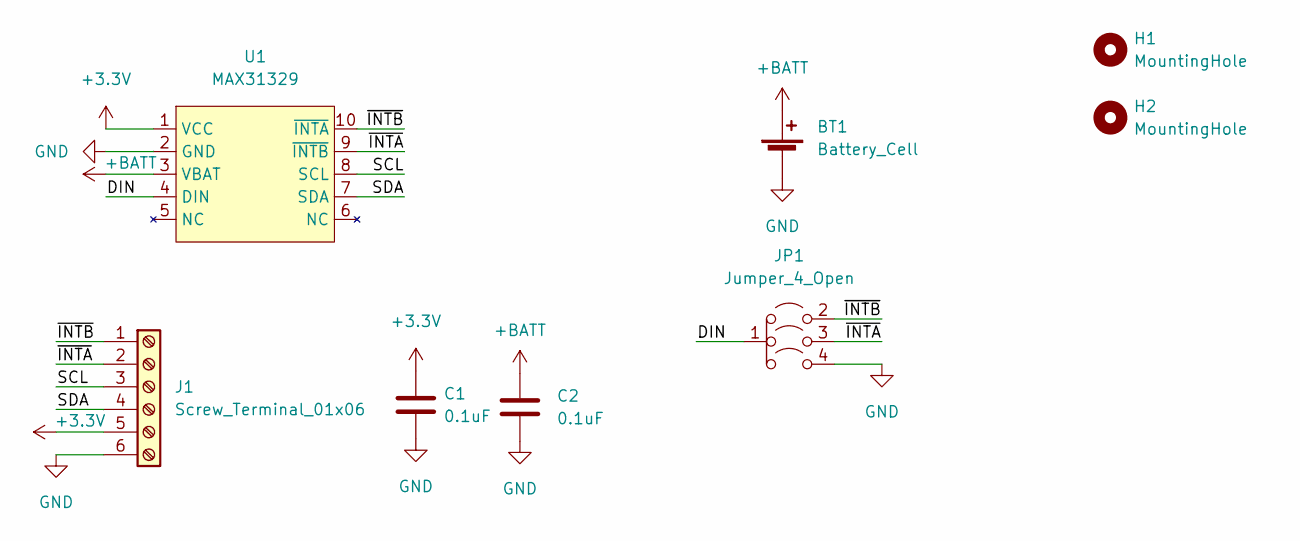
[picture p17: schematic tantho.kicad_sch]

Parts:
BT1: Battery_Cell; SMTM1225
C1, C2: 0.1uF; C_0603_1608Metric
H1, H2: MountingHole; MountingHole_3.2mm_M3
J1: Screw_Terminal_01x06; TerminalBlock_Phoenix_PT-1,5-6-3.5-H_1x06_P3.50mm_Horizontal
JP1: Jumper_4_Open; SolderJumper-4_Open_Pad1.0x1.5mm
U1: MAX31329; LGA10_5x5mm_21-100481

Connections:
+3.3V: C1.1, J1.5, U1.1 (VCC)
+BATT: BT1.1 (+), C2.1, U1.3 (VBAT)
/DIN: JP1.1 (A), U1.4 (DIN)
/SCL: J1.3, U1.8 (SCL)
/SDA: J1.4, U1.7 (SDA)
/~INTA: J1.2, JP1.3 (B), U1.9 (~INTB)
/~INTB: J1.1, JP1.2 (B), U1.10 (~INTA)
GND: BT1.2 (-), C1.2, C2.2, J1.6, JP1.4 (B), U1.2 (GND)

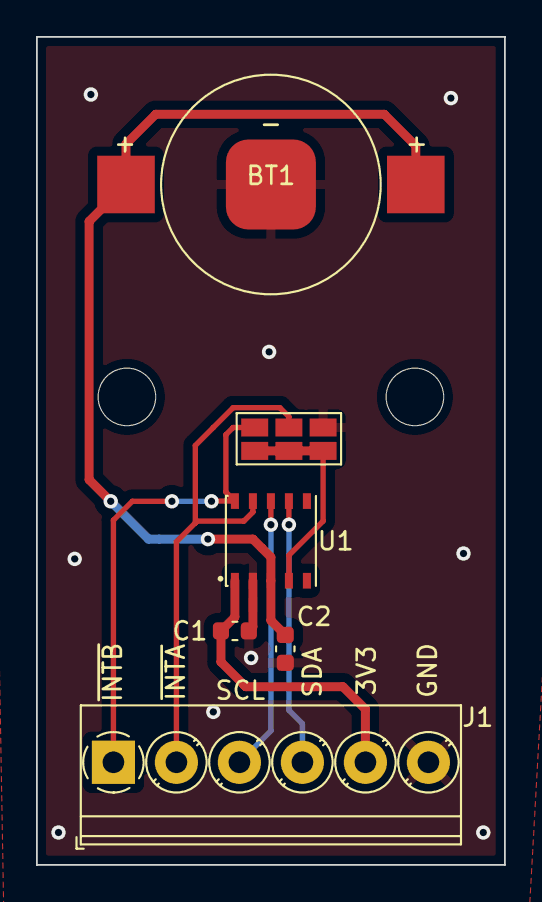
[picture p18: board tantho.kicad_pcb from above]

Board: 2 copper layers, 26.0 x 46.0 mm, 8 parts (0 on the bottom side), 8 nets.

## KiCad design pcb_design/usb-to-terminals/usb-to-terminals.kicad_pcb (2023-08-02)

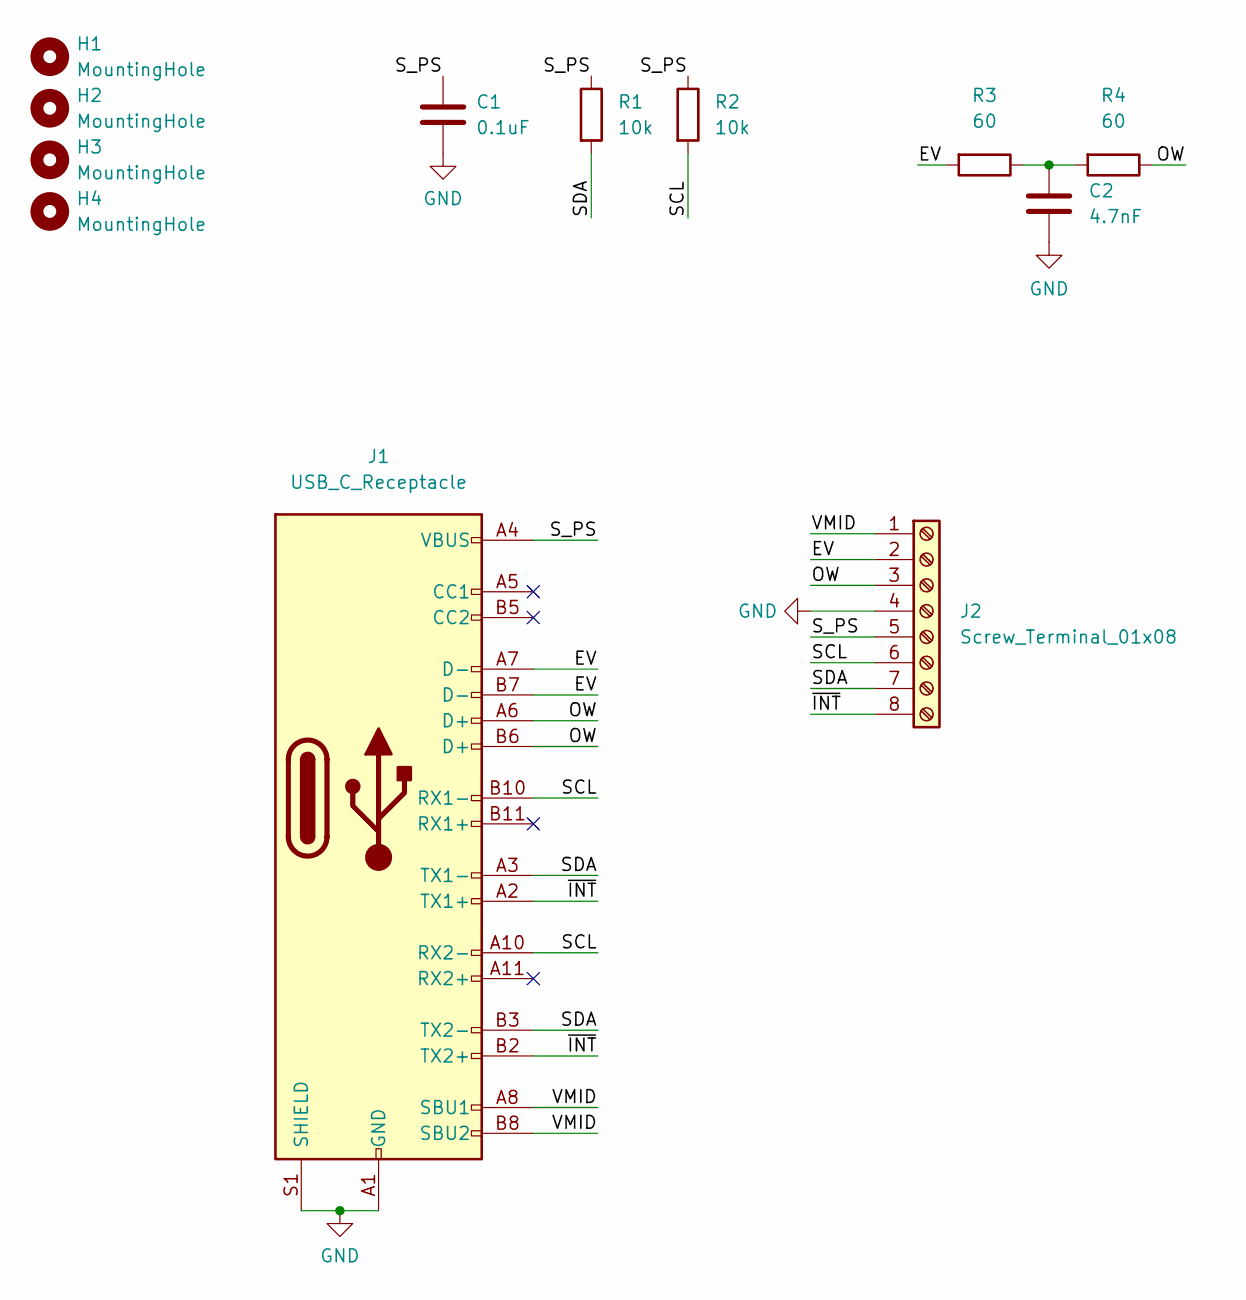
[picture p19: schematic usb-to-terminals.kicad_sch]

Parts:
C1: 0.1uF; C_0603_1608Metric; Voltage rating 16V; MPN C0603C104K4RAC7867
C2: 4.7nF; C_0603_1608Metric; Voltage rating 16V
H1, H2, H3, H4: MountingHole; MountingHole_3.2mm_M3
J1: USB_C_Receptacle; USB_C_Receptacle_Amphenol_12401861XX12A; MPN 124018612112A
J2: Screw_Terminal_01x08; TerminalBlock_Phoenix_PT-1,5-8-3.5-H_1x08_P3.50mm_Horizontal; MPN 1984646
R1, R2: 10k; R_0603_1608Metric
R3, R4: 60; R_0603_1608Metric

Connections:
/EV: J1.A7 (D-), J1.B7 (D-), J2.2, R3.2
/OW: J1.A6 (D+), J1.B6 (D+), J2.3, R4.1
/SCL: J1.A10 (RX2-), J1.B10 (RX1-), J2.6, R2.2
/SDA: J1.A3 (TX1-), J1.B3 (TX2-), J2.7, R1.2
/S_PS: C1.1, J1.A4 (VBUS), J1.A9 (VBUS), J1.B4 (VBUS), J1.B9 (VBUS), J2.5, R1.1, R2.1
/VMID: J1.A8 (SBU1), J1.B8 (SBU2), J2.1
/~INT: J1.A2 (TX1+), J1.B2 (TX2+), J2.8
GND: C1.2, C2.2, J1.A1 (GND), J1.A12 (GND), J1.B1 (GND), J1.B12 (GND), J1.S1 (SHIELD), J2.4
unnamed: C2.1, R3.1, R4.2

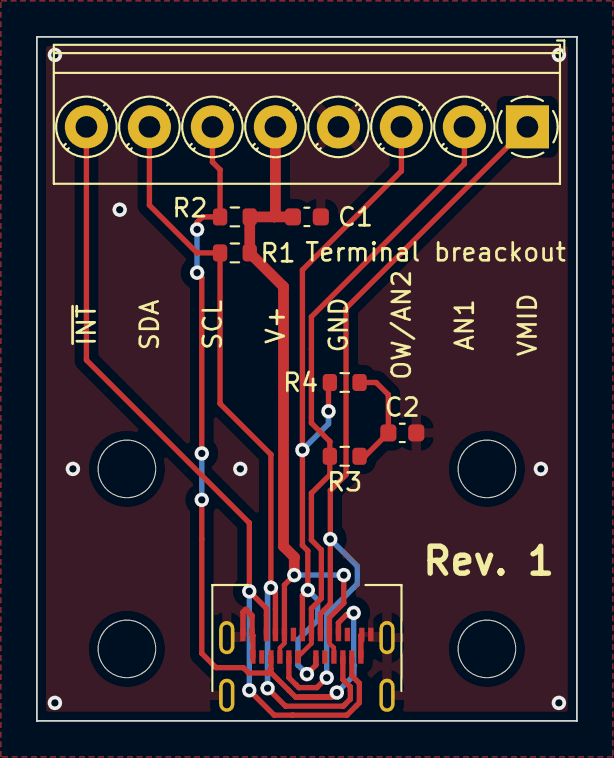
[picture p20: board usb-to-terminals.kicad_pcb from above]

Board: 2 copper layers, 30.0 x 38.0 mm, 12 parts (0 on the bottom side), 9 nets.

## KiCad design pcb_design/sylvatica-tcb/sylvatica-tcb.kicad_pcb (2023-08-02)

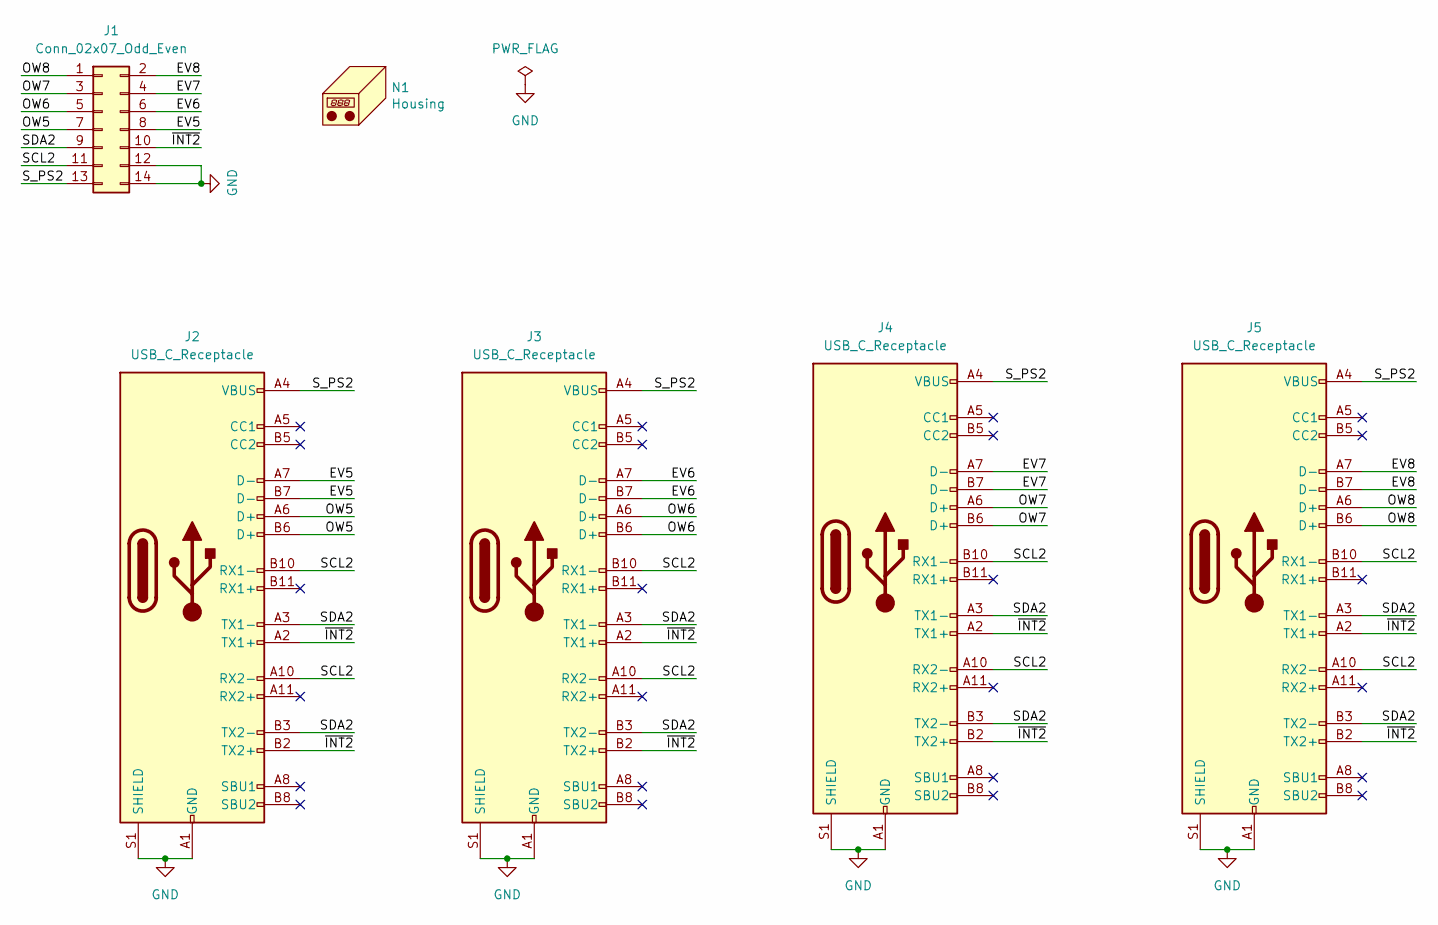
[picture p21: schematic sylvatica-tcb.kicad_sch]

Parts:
J1: Conn_02x07_Odd_Even; SAMTEC_TMMH-107-01-T-DV; MPN TMMH-107-01-T-DV
J2, J3, J4, J5: USB_C_Receptacle; USB_C_Receptacle_Amphenol_12401861XX12A; MPN 124018612112A
N1: Housing; Enclosure-Gloxinia4

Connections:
/EV5: J1.8, J2.A7 (D-), J2.B7 (D-)
/EV6: J1.6, J3.A7 (D-), J3.B7 (D-)
/EV7: J1.4, J4.A7 (D-), J4.B7 (D-)
/EV8: J1.2, J5.A7 (D-), J5.B7 (D-)
/OW5: J1.7, J2.A6 (D+), J2.B6 (D+)
/OW6: J1.5, J3.A6 (D+), J3.B6 (D+)
/OW7: J1.3, J4.A6 (D+), J4.B6 (D+)
/OW8: J1.1, J5.A6 (D+), J5.B6 (D+)
/SCL2: J1.11, J2.A10 (RX2-), J2.B10 (RX1-), J3.A10 (RX2-), J3.B10 (RX1-), J4.A10 (RX2-), J4.B10 (RX1-), J5.A10 (RX2-), J5.B10 (RX1-)
/SDA2: J1.9, J2.A3 (TX1-), J2.B3 (TX2-), J3.A3 (TX1-), J3.B3 (TX2-), J4.A3 (TX1-), J4.B3 (TX2-), J5.A3 (TX1-), J5.B3 (TX2-)
/S_PS2: J1.13, J2.A4 (VBUS), J2.A9 (VBUS), J2.B4 (VBUS), J2.B9 (VBUS), J3.A4 (VBUS), J3.A9 (VBUS), J3.B4 (VBUS), J3.B9 (VBUS), J4.A4 (VBUS), J4.A9 (VBUS), J4.B4 (VBUS), J4.B9 (VBUS), J5.A4 (VBUS), J5.A9 (VBUS), J5.B4 (VBUS), J5.B9 (VBUS)
/~INT2: J1.10, J2.A2 (TX1+), J2.B2 (TX2+), J3.A2 (TX1+), J3.B2 (TX2+), J4.A2 (TX1+), J4.B2 (TX2+), J5.A2 (TX1+), J5.B2 (TX2+)
GND: J1.12, J1.14, J2.A1 (GND), J2.A12 (GND), J2.B1 (GND), J2.B12 (GND), J2.S1 (SHIELD), J3.A1 (GND), J3.A12 (GND), J3.B1 (GND), J3.B12 (GND), J3.S1 (SHIELD), J4.A1 (GND), J4.A12 (GND), J4.B1 (GND), J4.B12 (GND), J4.S1 (SHIELD), J5.A1 (GND), J5.A12 (GND), J5.B1 (GND), J5.B12 (GND), J5.S1 (SHIELD)

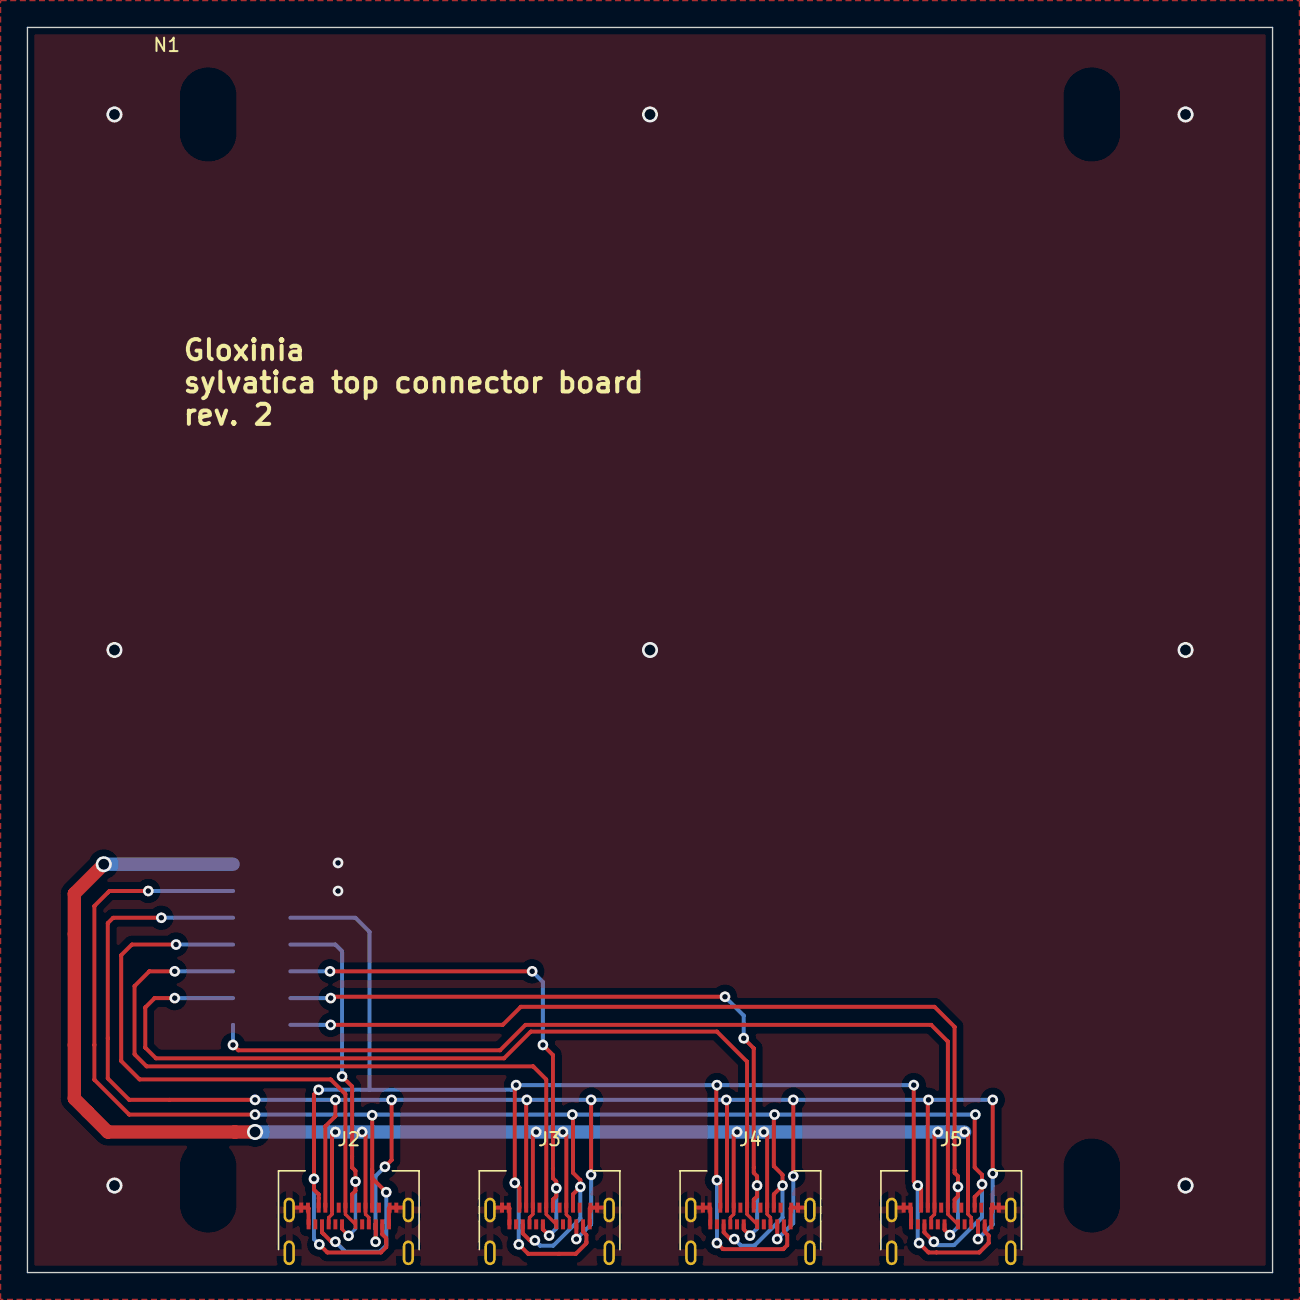
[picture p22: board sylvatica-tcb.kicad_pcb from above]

Board: 2 copper layers, 93.0 x 93.0 mm, 6 parts (1 on the bottom side), 13 nets.

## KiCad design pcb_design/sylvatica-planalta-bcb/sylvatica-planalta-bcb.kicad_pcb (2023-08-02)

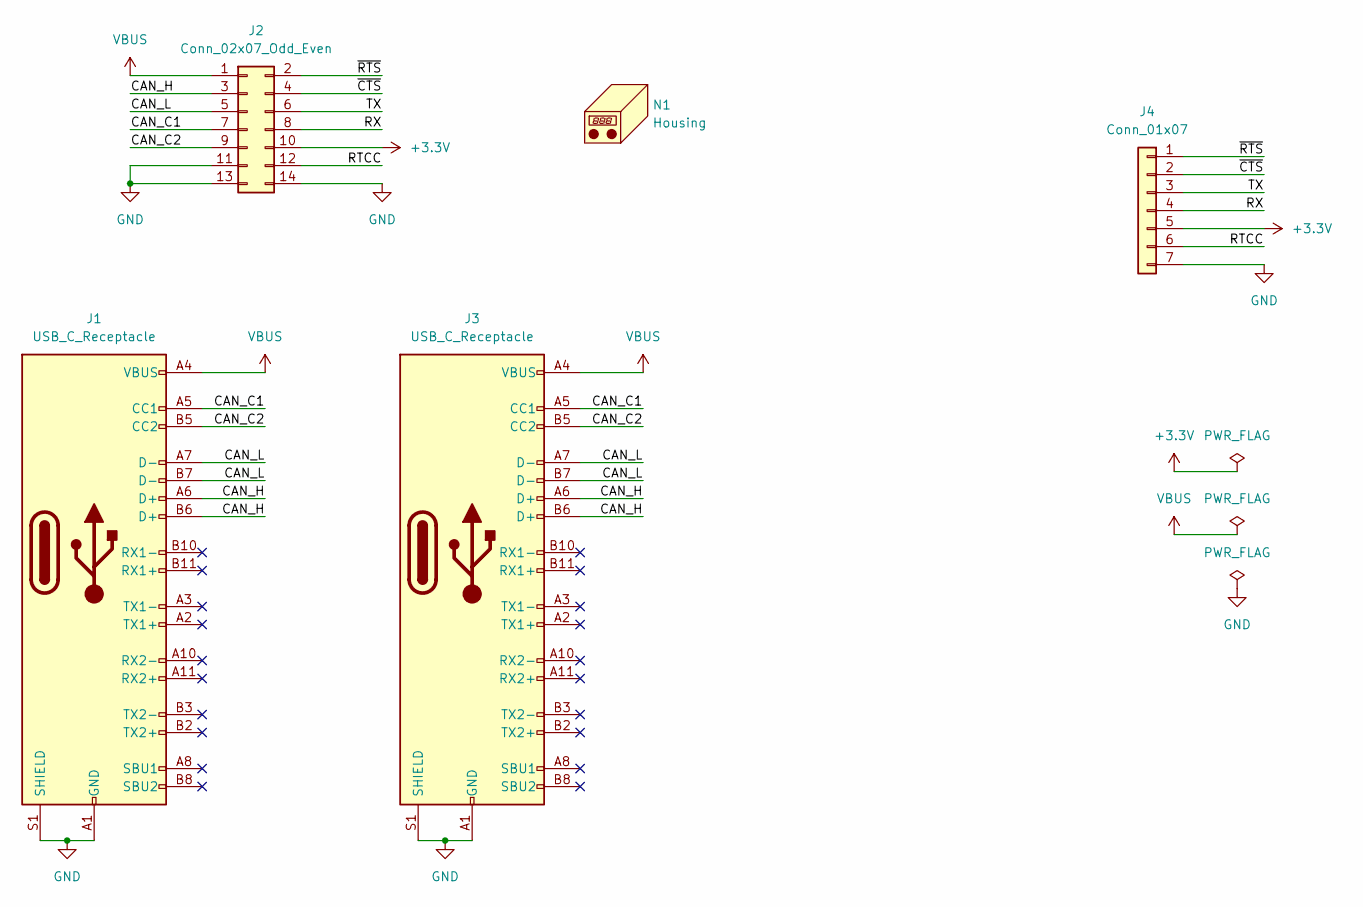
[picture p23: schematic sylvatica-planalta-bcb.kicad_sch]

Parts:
J1, J3: USB_C_Receptacle; USB_C_Receptacle_Amphenol_12401861XX12A; MPN 124018612112A
J2: Conn_02x07_Odd_Even; SAMTEC_MMS-107-02-F-DV; MPN MMS-107-02-F-DV
J4: Conn_01x07; PinHeader_1x07_P2.54mm_Vertical
N1: Housing; Enclosure-Gloxinia4

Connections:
+3.3V: J2.10, J4.5
/CAN_C1: J1.A5 (CC1), J2.7, J3.A5 (CC1)
/CAN_C2: J1.B5 (CC2), J2.9, J3.B5 (CC2)
/CAN_H: J1.A6 (D+), J1.B6 (D+), J2.3, J3.A6 (D+), J3.B6 (D+)
/CAN_L: J1.A7 (D-), J1.B7 (D-), J2.5, J3.A7 (D-), J3.B7 (D-)
/RTCC: J2.12, J4.6
/RX: J2.8, J4.4
/TX: J2.6, J4.3
/~CTS: J2.4, J4.2
/~RTS: J2.2, J4.1
GND: J1.A1 (GND), J1.A12 (GND), J1.B1 (GND), J1.B12 (GND), J1.S1 (SHIELD), J2.11, J2.13, J2.14, J3.A1 (GND), J3.A12 (GND), J3.B1 (GND), J3.B12 (GND), J3.S1 (SHIELD), J4.7
VBUS: J1.A4 (VBUS), J1.A9 (VBUS), J1.B4 (VBUS), J1.B9 (VBUS), J2.1, J3.A4 (VBUS), J3.A9 (VBUS), J3.B4 (VBUS), J3.B9 (VBUS)

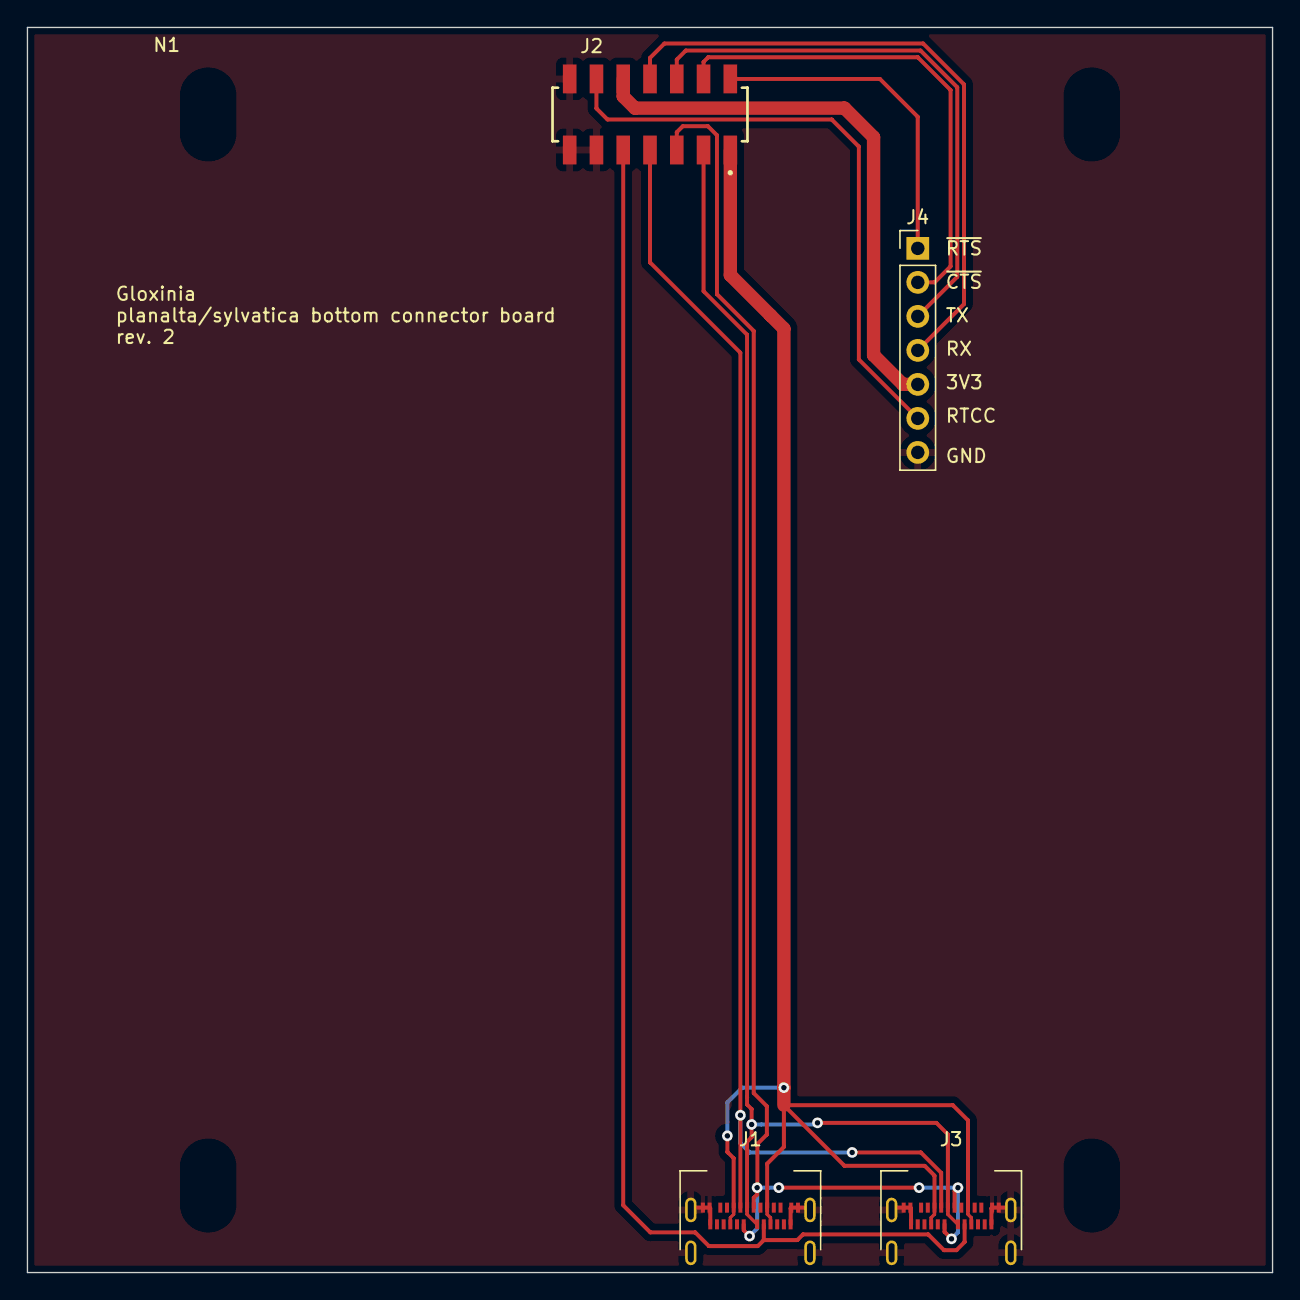
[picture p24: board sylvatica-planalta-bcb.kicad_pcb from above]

Board: 2 copper layers, 93.0 x 93.0 mm, 5 parts (0 on the bottom side), 12 nets.

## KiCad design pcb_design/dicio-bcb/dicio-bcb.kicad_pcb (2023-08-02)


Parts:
J1, J3, J4: USB_C_Receptacle; USB_C_Receptacle_Amphenol_12401861XX12A; MPN 124018612112A
J2: Conn_02x10_Odd_Even; SAMTEC-MMS-110-02-X-DV; MPN MMS-110-02-F-DV
J5: Conn_01x08; PinHeader_1x08_P2.54mm_Vertical
N1: Housing; Enclosure-Gloxinia4

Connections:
+3.3V: J2.11, J5.5
/CAN_C1: J2.8, J3.A5 (CC1), J4.A5 (CC1)
/CAN_C2: J2.6, J3.B5 (CC2), J4.B5 (CC2)
/CAN_H: J2.18, J3.A6 (D+), J3.B6 (D+), J4.A6 (D+), J4.B6 (D+)
/CAN_L: J2.16, J3.A7 (D-), J3.B7 (D-), J4.A7 (D-), J4.B7 (D-)
/CC1: J1.A5 (CC1), J2.3
/D+: J1.A6 (D+), J1.B6 (D+), J2.4
/D-: J1.A7 (D-), J1.B7 (D-), J2.2
/RTCC: J2.14, J5.7
/SYNC: J2.9, J5.6
/U1RX: J2.13, J5.4
/U1TX: J2.15, J5.3
/VCONN: J1.B5 (CC2), J2.1
/VUSBC: J1.A4 (VBUS), J1.A9 (VBUS), J1.B4 (VBUS), J1.B9 (VBUS), J2.10
/~U1CTS: J2.17, J5.2
/~U1RTS: J2.19, J5.1
GND: J1.A1 (GND), J1.A12 (GND), J1.B1 (GND), J1.B12 (GND), J1.S1 (SHIELD), J2.12, J3.A1 (GND), J3.A12 (GND), J3.B1 (GND), J3.B12 (GND), J3.S1 (SHIELD), J4.A1 (GND), J4.A12 (GND), J4.B1 (GND), J4.B12 (GND), J4.S1 (SHIELD), J5.8
VBUS: J2.20, J3.A4 (VBUS), J3.A9 (VBUS), J3.B4 (VBUS), J3.B9 (VBUS), J4.A4 (VBUS), J4.A9 (VBUS), J4.B4 (VBUS), J4.B9 (VBUS)


Board: 2 copper layers, 93.0 x 93.0 mm, 6 parts (0 on the bottom side), 18 nets.

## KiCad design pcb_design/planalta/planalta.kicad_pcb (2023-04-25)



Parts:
C1, C2, C48, C50: 120pF; C_0603_1608Metric; Mouser 80-C0603C121J5GAC
C3: 4.7nF; C_0603_1608Metric
C4, C33: 1uF; C_0603_1608Metric; Mouser 963-TMK325B7105KD-T
C5, C6, C7, C8, C14, C15, C16, C19, C21, C23, C24, C25, C26, C27, C28, C31, C32, C36, C37, C45, C52, C53, C54, C55, C70, C73, C74: 0.1uF; C_0603_1608Metric; Mouser 710-885012206071
C9, C18, C34, C35, C69, C71, C72: 1uF; C_0603_1608Metric; Mouser 81-GCM188R71C105K64D
C10, C22: 0.01uF; C_0603_1608Metric; Mouser 81-GRM033C81E103KE4E
C11, C20, C42, C44: 10uF; C_1210_3225Metric; Mouser 963-TMK325BJ106KM-P
C12, C68: 2.2uF; C_1206_3216Metric; Mouser 791-1206X225K250CT
C13: 4.7uF; C_1206_3216Metric; Mouser 81-GCG31CR71E475JA1L
C17: 22uF; C_1206_3216Metric; Mouser 963-TMK316BBJ226ML-T
C29, C38: 4.7uF; C_1206_3216Metric
C30: 1nF; C_0603_1608Metric
C39, C41: 82nF; C_0603_1608Metric; Mouser 80-C0603C823J3R
C40, C43: 680nF; C_0603_1608Metric; Mouser 710-885012206051
C46, C47: 10pF; C_0603_1608Metric; Mouser 603-CC603FRNPO9BN100
C49, C51, C65, C66: 1.5nF; C_0603_1608Metric; Mouser 710-885012206035
C56, C60: 270nF; C_0603_1608Metric; Mouser 80-C0603C274K8P
C57, C58, C59, C61: 470nF; C_0603_1608Metric; Mouser 710-885012206075
C62, C64: 1nF; C_0603_1608Metric; Mouser 963-TMK325B7105KD-T
C63, C67: 1.2nF; C_0603_1608Metric; Mouser 81-GRM1885C1H122JA01
D1, D2: LED; LED_0603_1608Metric; Mouser 78-TLMS1000
J1, J2, J3, J4: USB_C_Receptacle; USB_C_Receptacle_Amphenol_12401861XX12A
J5: Conn_02x07_Odd_Even; SAMTEC_TMMH-107-01-T-DV
J9: Conn_01x06_Female; PinSocket_1x06_P2.54mm_Vertical
N1: Housing; Enclosure-Gloxinia4; Mouser 546-1554LA2GYCL
Q1, Q2, Q4, Q5: Q_NMOS_GSD; SOT-23; Mouser 512-BSS138
Q3: Q_NMOS_GSD; SOT-23; Mouser 771-PMV20XNER
R1, R2, R11, R21, R28, R32: 6.8k; R_0603_1608Metric; Mouser 667-ERJ-3RBD6801V
R3: 1k; R_0603_1608Metric
R4, R33: 60R; R_0603_1608Metric; Mouser 594-5063JD120R0F
R5, R7: 20; R_0603_1608Metric; Mouser 71-CRCW060320R0FKEAC
R6, R8: 12; R_0603_1608Metric; Mouser 667-ERJ-3EKF15R0V
R9, R10, R15, R16, R19, R34, R35, R38, R41, R42: 10k; R_0603_1608Metric; Mouser 284-APC0603B10K0N
R12, R14: 0.22R; R_0603_1608Metric; Mouser 667-ERJ-3RQFR22V
R13: 1k; R_0603_1608Metric; Mouser 652-CR0603-FX1001HLF
R17, R18: 750; R_0603_1608Metric; Mouser 603-RC0603FR-07750RL
R20, R22: 2.7k; R_0603_1608Metric; Mouser 603-AC0603FR-102K7L
R23, R25: 15; R_0603_1608Metric; Mouser 667-ERJ-3EKF15R0V
R24, R26, R29, R30: 33; R_0603_1608Metric; Mouser 71-CRCW060333R0FKEAC
R27, R31: 1.6k; R_0603_1608Metric; Mouser 603-RC0603FR-071K6L
R36: 270; R_0603_1608Metric; Mouser 603-RC0603FR-07270RL
R37: 1M; R_0603_1608Metric; Mouser 603-RC0603FR-101ML
R39, R40: 4.3k; R_0603_1608Metric
R43, R44, R45, R46, R47, R48: 10k; R_0603_1608Metric
SW1: SW_Push; SW_SPST_KMR2; Mouser 611-KMR621NGLFS
U1, U2, U3, U4: MAX4475_var; SOT-23-6; Mouser 700-MAX4475AUT+T
U5, U6, U15, U16: PGA113; MSOP-10_3x3mm_P0.5mm; Mouser 595-PGA113AIDGSR
U7: MCP2542FD; SOIC-8_3.9x4.9mm_P1.27mm; Mouser 579-MCP2542FDT-E/SN
U8: ADM7170; LFCSP-8-1EP_3x3mm_P0.5mm_EP1.45x1.74mm
U9: ADS8332; TSSOP-24_4.4x7.8mm_P0.65mm; Mouser 595-ADS8332IBPWR
U10: dsPIC33EP512MC806; TQFP-64_10x10mm_P0.5mm; Mouser 579-33EP512MC806IPT
U11, U21, U22, U23: DG2034E; MSOP-10_3x3mm_P0.5mm; Mouser 78-DG2034EDQ-T1-GE3
U12: LP2985-5.0; SOT-23-5; Mouser 926-LP2985IM540NOPB
U13: REF2033; SOT-23-5; Mouser 595-REF2033AIDDCR
U14: OPA320; SOT-23-5; Mouser 595-OPA320AIDBVR
U17: TPS737; SOT-223-6; Mouser 595-TPS73733DCQR
U18, U19, U20, U24, U25: SiP32431; SOT-363_SC-70-6; Mouser 781-SIP32431DR3-GE3
Y1: Crystal_GND24; Crystal_SMD_Abracon_ABM3B-4Pin_5.0x3.2mm; Mouser 520-80-10-30B-CWNT

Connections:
+3.3V: C7.2, C8.2, C14.2, C16.2, C19.1, C21.1, C31.2, C32.2, C42.1, C45.1, C68.1, C71.1, J5.12, J9.2, Q1.1 (G), Q2.1 (G), Q4.1 (G), Q5.1 (G), R9.1, R15.1, R17.2, R19.1, R35.1, R38.1, R43.1, R44.1, R45.1, R46.1, R47.1, R48.1, U5.10 (DVDD), U6.10 (DVDD), U7.5 (VIO), U9.16 (VBD), U10.10 (VDD), U10.19 (AVDD), U10.26 (VDD), U10.38 (VDD), U10.57 (VDD), U15.10 (DVDD), U16.10 (DVDD), U17.2 (OUT), U24.4 (IN)
+4V: C5.2, C6.2, C12.1, C18.1, C23.2, C24.2, C44.2, R16.1, U5.1 (AVDD), U6.1 (AVDD), U9.17 (VA), U12.5 (VOUT), U13.4 (V_IN), U14.5 (V+), U15.1 (AVDD), U16.1 (AVDD)
/BLK: R18.2, U10.44 (ASCL1/PMCS2/RPI74/RD10)
/C1RX: U7.4 (RX), U10.58 (RP96/RF0)
/C1TX: U7.1 (TX), U10.60 (AN24/PWM1L/PMD0/RP80/RE0)
/CAN_C1: J5.7, U10.22 (AN9/PMA7/RPI41/RB9)
/CAN_C2: J5.9, U10.21 (AN8/PMA6/RPI40/RB8)
/CAN_H: J5.3, Q3.3 (D), U7.7 (CANH)
/CAN_L: J5.5, R33.1, U7.6 (CANL)
/CHS0: U10.17 (PGEC1/AN6/RPI38/RB6), U11.1 (A0), U21.1 (A0), U22.1 (A0), U23.1 (A0)
/CHS1: U10.18 (PGED1/AN7/RPI39/RB7), U11.10 (A1), U21.10 (A1), U22.10 (A1), U23.10 (A1)
/CIN1: J1.A7 (D-), J1.B7 (D-), U15.2 (CH1)
/CIN2: J2.A7 (D-), J2.B7 (D-), U16.2 (CH1)
/CIN3: J3.A7 (D-), J3.B7 (D-), U5.2 (CH1)
/CIN4: J4.A7 (D-), J4.B7 (D-), U6.2 (CH1)
/DRV1: R11.1, R20.2, R27.2, R28.1, U10.34 (RP98/RF2)
/DRV2: R21.1, R22.2, R31.2, R32.1, U10.33 (RP99/RF3)
/DRV3: R39.2, U10.62 (AN26/PWM2L/PMD2/RP82/RE2)
/DRV4: R40.2, U10.64 (AN28/PWM3L/PMD4/RP84/RE4)
/EN: R34.2, U17.5 (EN)
/EN_LDO4: Q1.3 (D), R10.2, U12.3 (ON/~OFF)
/EN_REFH: Q2.3 (D), R16.2, U13.3 (EN)
/EN_REFL: Q2.2 (S), R15.2, U10.63 (AN27PWM2H/PMD3/RPI83/RE3)
/EN_VA: U8.5 (EN), U10.28 (TDI/AN13/PMA10/RPI45/RB13)
/EN_VDDA: Q1.2 (S), R9.2, U10.61 (AN25/PWM1H/PMD1/RPI81/RE1)
/FIN1: U9.7 (IN7), U11.8 (COM)
/FIN2: U9.5 (IN5), U21.8 (COM)
/FIN3: C58.1, R29.1, U9.3 (IN3)
/FIN4: C59.1, R30.1, U9.1 (IN1)
/FOUT1: R1.2, U22.8 (COM)
/FOUT2: R2.2, U23.8 (COM)
/FOUT3: C65.1, R39.1, U3.3 (IN+)
/FOUT4: C66.1, R40.1, U4.3 (IN+)
/IN1: R5.1, R6.2, R23.2, R24.1, U15.5 (VOUT)
/IN2: R7.1, R8.2, R25.2, R26.1, U16.5 (VOUT)
/IN3: R29.2, U5.5 (VOUT)
/IN4: R30.2, U6.5 (VOUT)
/OSC_IN: C47.1, R37.2, U10.39 (OSC1/RPI60/RC12), Y1.3
/OUT1: J1.A6 (D+), J1.B6 (D+), U1.1 (OUT), U1.4 (IN-), U9.6 (IN6)
/OUT2: J2.A6 (D+), J2.B6 (D+), U2.1 (OUT), U2.4 (IN-), U9.4 (IN4)
/OUT3: J3.A6 (D+), J3.B6 (D+), U3.1 (OUT), U3.4 (IN-), U9.2 (IN2)
/OUT4: J4.A6 (D+), J4.B6 (D+), U4.1 (OUT), U4.4 (IN-), U9.24 (IN0)
/PGC: J9.5, U10.48 (PGEC2/SOSCO/C3IN1-/T1CK/RPI62/RC14)
/PGD: J9.4, U10.47 (PGED2/SOSCI/C3IN3-/RPI61/RC13)
/PWR1: C70.1, U5.4 (VREF), U6.4 (VREF), U15.4 (VREF), U16.4 (VREF), U20.1 (OUT)
/REF+1: C11.2, C69.1, R14.1, U9.18 (REF+), U14.1 (OUT), U14.4 (-IN), U20.4 (IN)
/REF+2: C34.1, C35.1, U13.1 (V_BIAS), U18.4 (IN), U19.4 (IN)
/REF_C1: U10.11 (AN5/C1IN1+/RPI37/RB5), U18.3 (ON/OFF), U19.3 (ON/OFF), U20.3 (ON/OFF)
/RPGA1: C37.1, U5.3 (VCAL/CH0), U6.3 (VCAL/CH0), U15.3 (VCAL/CH0), U16.3 (VCAL/CH0), U19.1 (OUT)
/RTCC: J5.10, U10.42 (RTCC/RPI72/RD8)
/RX: J5.8, U10.52 (PWMR/RP68/RD4)
/SCK_ADC: U9.10 (SCLK), U10.4 (C1IN3-/SCK2/PMA5/RP118/RG6)
/SCK_PGA: U5.7 (SCLK), U6.7 (SCLK), U10.54 (C3IN2-/RP70/RD6), U15.7 (SCLK), U16.7 (SCLK)
/SCL1: J1.A10 (RX2-), J1.B10 (RX1-), J2.A10 (RX2-), J2.B10 (RX1-), R43.2, U10.37 (SCL1/RG2)
/SCL2: J3.A10 (RX2-), J3.B10 (RX1-), J4.A10 (RX2-), J4.B10 (RX1-), R45.2, U10.32 (SCL2/PMA8/RP101/RF5)
/SDA1: J1.A3 (TX1-), J1.B3 (TX2-), J2.A3 (TX1-), J2.B3 (TX2-), R44.2, U10.36 (SDA1/RG3)
/SDA2: J3.A3 (TX1-), J3.B3 (TX2-), J4.A3 (TX1-), J4.B3 (TX2-), R46.2, U10.31 (SDA2/PMA9/RP100/RF4)
/SDI_ADC: U9.13 (SDO), U10.5 (C1IN1-/SDI2/PMA4/RPI119/RG7)
/SDO_ADC: U9.12 (SDI), U10.6 (C2IN3-/SDO2/PMA3/RP120/RG8)
/SDO_PGA: U5.8 (DIO), U6.8 (DIO), U10.53 (PMRD/RP69/RD5), U15.8 (DIO), U16.8 (DIO)
/S_PS: C73.1, C74.1, J1.A4 (VBUS), J1.A9 (VBUS), J1.B4 (VBUS), J1.B9 (VBUS), J2.A4 (VBUS), J2.A9 (VBUS), J2.B4 (VBUS), J2.B9 (VBUS), J3.A4 (VBUS), J3.A9 (VBUS), J3.B4 (VBUS), J3.B9 (VBUS), J4.A4 (VBUS), J4.A9 (VBUS), J4.B4 (VBUS), J4.B9 (VBUS), U24.1 (OUT), U25.1 (OUT)
/S_PS_A_EN: U10.46 (INT0/RP64/RD0), U25.3 (ON/OFF)
/S_PS_D_EN: U10.45 (PMCS1/RPI75/RD11), U24.3 (ON/OFF)
/TERM: R3.2, U10.55 (C3IN1+/RP71/RD7)
/TX: J5.6, U10.51 (PMBE/RP67/RD3)
/VMID: C36.1, J1.A8 (SBU1), J1.B8 (SBU2), J2.A8 (SBU1), J2.B8 (SBU2), J3.A8 (SBU1), J3.B8 (SBU2), J4.A8 (SBU1), J4.B8 (SBU2), U18.1 (OUT)
/~CNV_ADC: U9.15 (~CONVST), U10.3 (AN31/PWM4H/PMD7/RP87/RE7)
/~CS1: U10.29 (AN14/PMA1/RPI46/RB14), U15.9 (~CS)
/~CS2: U10.14 (AN2/C2IN2-/VMIO/RPI34/RB2), U16.9 (~CS)
/~CS3: U5.9 (~CS), U10.16 (PGED3/AN0/VREF+/RPI32/RB0)
/~CS4: U6.9 (~CS), U10.15 (PGEC3/AN1/VREF-/RPI33/RB1)
/~CS_ADC: U9.11 (FS/~CS), U10.1 (AN29/PWM3H/PMD5/RP85/RE5)
/~CTS: J5.4, U10.50 (RP66/RD2)
/~INT1: J1.A2 (TX1+), J1.B2 (TX2+), J2.A2 (TX1+), J2.B2 (TX2+), R47.2, U10.35 (RP102/RF6)
/~INT2: J3.A2 (TX1+), J3.B2 (TX2+), J4.A2 (TX1+), J4.B2 (TX2+), R48.2, U10.2 (AN30/PWM4L/PMD6/RPI86/RE6)
/~INT_ADC: U9.9 (EOC/~INT/CDI), U10.12 (AN4/C1IN2-/RPI36/RB4)
/~MCLR: C22.1, J9.1, R19.2, R36.2, SW1.2
/~RST_ADC: U9.8 (~RESET), U10.13 (AN3/C2IN1+/VPIO/RPI35/RB3)
/~RTS: J5.2, U10.49 (RP65/RD1)
/~SD1: Q4.3 (D), R41.2, U1.5 (~SHDN), U2.5 (~SHDN)
/~SD1_L: Q4.2 (S), R35.2, U10.59 (RP97/RF1)
/~SD2: Q5.3 (D), R42.2, U3.5 (~SHDN), U4.5 (~SHDN)
/~SD2_L: Q5.2 (S), R38.2, U10.8 (C2IN1-/PMA2/RPI121/RG9)
GND: C1.2, C2.2, C3.2, C4.2, C5.1, C6.1, C7.1, C8.1, C9.2, C10.2, C11.1, C12.2, C13.2, C14.1, C15.2, C16.1, C17.2, C18.2, C19.2, C20.2, C21.2, C22.2, C23.1, C24.1, C25.1, C26.1, C27.1, C28.1, C29.2, C30.2, C31.1, C32.1, C33.2, C34.2, C35.2, C36.2, C37.2, C38.2, C39.1, C40.2, C41.1, C42.2, C43.2, C44.1, C45.2, C46.1, C47.2, C48.1, C49.2, C50.1, C51.2, C52.1, C53.1, C54.1, C55.1, C56.2, C57.1, C58.2, C59.2, C60.2, C61.1, C62.2, C63.1, C64.2, C65.2, C66.2, C67.1, C68.2, C69.2, C70.2, C71.2, C72.2, C73.2, C74.2, D1.1 (K), D2.1 (K), J1.A1 (GND), J1.A12 (GND), J1.B1 (GND), J1.B12 (GND), J1.S1 (SHIELD), J2.A1 (GND), J2.A12 (GND), J2.B1 (GND), J2.B12 (GND), J2.S1 (SHIELD), J3.A1 (GND), J3.A12 (GND), J3.B1 (GND), J3.B12 (GND), J3.S1 (SHIELD), J4.A1 (GND), J4.A12 (GND), J4.B1 (GND), J4.B12 (GND), J4.S1 (SHIELD), J5.11, J5.13, J5.14, J9.3, SW1.1, U1.2 (VSS), U2.2 (VSS), U3.2 (VSS), U4.2 (VSS), U5.6 (GND), U6.6 (GND), U7.2 (VSS), U7.8 (STBY), U8.6 (GND), U8.9 (PAD), U9.14 (DGND), U9.19 (REF-), U9.20 (AGND), U9.23 (COM), U10.9 (VSS), U10.20 (AVSS), U10.25 (VSS), U10.41 (VSS), U11.3 (GND), U12.2 (GND), U13.2 (GND), U14.2 (V-), U15.6 (GND), U16.6 (GND), U17.3 (GND), U17.6 (TAB), U18.2 (GND), U18.5 (GND), U19.2 (GND), U19.5 (GND), U20.2 (GND), U20.5 (GND), U21.3 (GND), U22.3 (GND), U23.3 (GND), U24.2 (GND), U24.5 (GND), U25.2 (GND), U25.5 (GND), Y1.2, Y1.4
unnamed: C1.1, R1.1, U1.3 (IN+)
unnamed: C2.1, R2.1, U2.3 (IN+)
unnamed: C3.1, R4.1, R33.2
unnamed: C10.1, U12.4 (BP)
unnamed: C13.1, R12.2
unnamed: C15.1, R13.1, U14.3 (+IN)
unnamed: C17.1, R14.2
unnamed: C20.1, U10.56 (VCAP)
unnamed: C30.1, U8.4 (SS)
unnamed: C33.1, U17.4 (NC/FB)
unnamed: C39.2, R5.2, U11.2 (S1)
unnamed: C40.1, R6.1, U11.4 (S3)
unnamed: C41.2, R7.2, U21.2 (S1)
unnamed: C43.1, R8.1, U21.4 (S3)
unnamed: C46.2, R37.1, U10.40 (OSC2/CLKO/RC15), Y1.1
unnamed: C48.2, R11.2, U22.2 (S1)
unnamed: C49.1, R20.1, U22.4 (S3)
unnamed: C50.2, R21.2, U23.2 (S1)
unnamed: C51.1, R22.1, U23.4 (S3)
unnamed: C56.1, R23.1, U11.9 (S2)
unnamed: C57.2, R24.2, U11.7 (S4)
unnamed: C60.1, R25.1, U21.9 (S2)
unnamed: C61.2, R26.2, U21.7 (S4)
unnamed: C62.1, R27.1, U22.9 (S2)
unnamed: C63.2, R28.2, U22.7 (S4)
unnamed: C64.1, R31.1, U23.9 (S2)
unnamed: C67.2, R32.2, U23.7 (S4)
unnamed: D1.2 (A), R17.1
unnamed: D2.2 (A), R18.1
unnamed: Q3.1 (G), R3.1
unnamed: Q3.2 (S), R4.2
unnamed: R12.1, R13.2, U13.5 (V_REF)
unnamed: R36.1, U10.7 (~MCLR)
unnamed: U9.21 (ADCIN), U9.22 (MUXOUT)
VBUS: C4.1, C9.1, C25.2, C26.2, C27.2, C28.2, C38.1, C52.2, C53.2, C54.2, C55.2, J5.1, R10.1, R34.1, R41.1, R42.1, U1.6 (VDD), U2.6 (VDD), U3.6 (VDD), U4.6 (VDD), U7.3 (VDD), U8.7 (VIN), U8.8 (VIN), U11.5 (EN), U11.6 (V+), U12.1 (VIN), U17.1 (IN), U21.5 (EN), U21.6 (V+), U22.5 (EN), U22.6 (V+), U23.5 (EN), U23.6 (V+)
VDDA: C29.1, C72.1, U8.1 (VOUT), U8.2 (VOUT), U8.3 (SENSE), U25.4 (IN)

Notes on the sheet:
Reference generation
Analog signal voltage level conversion
Programming and debug interface
Input signal amplification

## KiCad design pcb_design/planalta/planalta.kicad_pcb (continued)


Board: 2 copper layers, 93.0 x 93.0 mm, 163 parts (1 on the bottom side), 120 nets.

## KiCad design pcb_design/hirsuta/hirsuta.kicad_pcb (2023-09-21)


Board: 2 copper layers, 40.0 x 44.0 mm, 31 parts (0 on the bottom side), 26 nets.

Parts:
C1, C2, C3, C4: 0.1uF; C_0603_1608Metric
C5, C7: 2.2uF; C_1206_3216Metric
C6, C8, C9, C10, C11, C12: C; C_0603_1608Metric
H1, H2: MountingHole; MountingHole_3.2mm_M3
J1: Screw_Terminal_01x08; TerminalBlock_Phoenix_PT-1,5-8-3.5-H_1x08_P3.50mm_Horizontal
J2: Screw_Terminal_01x11; TerminalBlock_Phoenix_PT-1,5-11-3.5-H_1x11_P3.50mm_Horizont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
JP1, JP2, JP3, JP4, JP5, JP6, JP7: Jumper_3_Open; SolderJumper-3_P1.3mm_Open_Pad1.0x1.5mm
R1, R2, R3, R4, R5, R6: R; C_0603_1608Metric
U1: ADS1219; TSSOP-16-1EP_4.4x5mm_P0.65mm
U2: ADP7142AUJZ-1.8; TSOT-23-5

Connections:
+3.3V: C4.1, J2.8, JP2.1 (A), JP4.3 (B), JP5.3 (B), JP7.1 (A), U1.13 (DVDD)
+5V: C5.1, J2.10, U2.1 (VIN), U2.3 (EN)
/A0: JP1.2 (C), JP2.2 (C), U1.1 (A0)
/A1: JP6.2 (C), JP7.2 (C), U1.2 (A1)
/AIN01+: J1.6, R6.1
/AIN01-: J1.5, R4.1
/AIN01P+: C8.1, C9.2, R6.2, U1.11 (AIN0)
/AIN01P-: C8.2, C10.1, R4.2, U1.10 (AIN1)
/AIN23+: J1.8, R5.1
/AIN23-: J1.7, R3.1
/AIN23P+: C6.1, C11.2, R5.2, U1.7 (AIN2)
/AIN23P-: C6.2, C12.1, R3.2, U1.6 (AIN3)
/AVDD: C3.1, JP5.2 (C), U1.12 (AVDD)
/AVDD_H: J1.4, J2.7, JP5.1 (A)
/POWER: C7.1, J1.1, R1.1, U2.5 (VOUT)
/REFN: C1.1, JP3.2 (C), U1.8 (REFN)
/REFN_H: J2.5, JP3.1 (A)
/REFP: C2.1, JP4.2 (C), U1.9 (REFP)
/REFP_H: J2.6, JP4.1 (A)
/SCL: J2.3, JP1.1 (A), JP6.1 (A), U1.16 (SCL)
/SDA: J2.2, JP1.3 (B), JP6.3 (B), U1.15 (SDA)
/~DRDY: J2.1, U1.14 (~DRDY)
/~RESET: J2.4, U1.3 (~RESET)
GND: C1.2, C2.2, C3.2, C4.2, C9.1, C10.2, C11.1, C12.2, J1.3, J2.9, JP2.3 (B), JP3.3 (B), JP7.3 (B), U1.4 (DGND), U1.5 (AGND)
GND1: C5.2, C7.2, J1.2, J2.11, R2.2, U2.2 (GND)
unnamed: R1.2, R2.1, U2.4 (SENSE/ADJ)

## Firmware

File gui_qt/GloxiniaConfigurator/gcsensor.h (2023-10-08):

#ifndef GCSENSOR_H
#define GCSENSOR_H

#include <Qt>
#include <QString>
#include <QList>
#include <QAbstractItemModel>
#include <QFile>
#include "gmessage.h"
#include "gcnode.h"
#include <QLineSeries>

class GCSensor
{

public:
    GCSensor(GCNode* const node = nullptr, quint8 ifid = 0x0, quint8 id = 0x0);
    virtual ~GCSensor();

    enum sensor_class
    {
        NOT_SET = 0x00,
        SHT35 = 0x01,
        APDS9306_065 = 0x02,
        ADC12 = 0x03,
        ADC16 = 0x04,
        LIA = 0x05,
        ADS1219 = 0x06,
    };

    enum GCSensorStatus
    {
        INACTIVE = 0x00,
        IDLE = 0x01,
        ACTIVE = 0x02,
        RUNNING = 0x03,
        STOPPED = 0x04,
        ERROR = 0x05
    };

    enum VariableType {
        Temperature,
        RelativeHumidity,
        Light,
        Analogue,
    };

    enum PGAGain
    {
        PGA_GAIN_1 = 0b0000,   ///< Gain = 1
        PGA_GAIN_2 = 0b0001,   ///< Gain = 2
        PGA_GAIN_5 = 0b0010,   ///< Gain = 5
        PGA_GAIN_10 = 0b0011,  ///< Gain = 10
        PGA_GAIN_20 = 0b0100,  ///< Gain = 20
        PGA_GAIN_50 = 0b0101,  ///< Gain = 50
        PGA_GAIN_100 = 0b0110, ///< Gain = 100
        PGA_GAIN_200 = 0b0111, ///< Gain = 200
    };

    // static QString sensorTypeToString(SensorType t);

    quint8 getSensorID(void);
    quint8 getInterfaceID(void);

    GCNode* getNode(void) const;

    QString getLabel(void) const;
    void setLabel(const QString label);
    quint16 getMeasurementPeriod(void) const;
    void setMeasurementPeriod(quint16 period);
    bool getUseGlobalPeriodFlag(void) const;
    void setUseGlobalPeriodFlag(bool flag);
    void setStatus(GCSensorStatus s);
    GCSensorStatus getStatus() const;
    QList<VariableType> getVariableTypes() const;
    QList<QLineSeries*> getPlotSeries() const;

    static GCSensor* fromQVariant(const QVariant data);

    static QString statusToString(GCSensorStatus s);

    virtual bool startMeasurement(void);
    GMessage getStartMessage(void);
    GMessage getStopMessage(void);
    virtual void stopMeasurement(void);
    virtual void saveData(std::vector<quint8>& data) = 0;
    virtual void printHeader(void) = 0;

    friend QDebug operator<<(QDebug dbg, const GCSensor &);

    virtual QString toString(void) const = 0;
    virtual QString toConfigString(void) const = 0;
    virtual bool fromConfigString(const QStringList &config) = 0;
    virtual QList<GMessage> getConfigurationMessages() = 0;

    friend QDataStream &operator<<(QDataStream &out, const GCSensor &myObj);
    friend QDataStream &operator>>(QDataStream &in, GCSensor &myObj);

    static void setSensorFileDir(const QString dir);
    static QString getSensorFileDir(void);

    static QString VariableTypeToString(VariableType t);

    unsigned int getMaxPlotSize(void);
    void setMaxPlotSize(unsigned int value);

    static int getFullID(short interface, short sensor);

protected:
    GCNode* const node;
    const quint8 sensorID;
    const quint8 interfaceID;

    GCSensorStatus status = INACTIVE;
    quint16 measurementPeriod = 9;
    bool useGlobalPeriod = false;
    QString label;
    QFile* file = nullptr;
    QString filePath;

    static QString sensorFileDir;
    unsigned int maxPlotSize = 100;

    // data storage for plotting
    QList<QLineSeries*> plotSeries;
    QList<VariableType> measurementVariableTypes;
};

Q_DECLARE_METATYPE(GCSensor *)

class GCSensorI2C : public GCSensor
{
public:
    GCSensorI2C(GCNode* const node = nullptr, quint8 interface_id=0, quint8 id = 0, quint8 i2cAddress = 0x0);
    virtual ~GCSensorI2C() = 0;

    virtual bool setI2CAddress(const quint8 a);

    const quint8 getI2CAddress(void);

    virtual int i2cAddressToInt(quint8 a);

    virtual QString toString(void) const = 0;
    virtual QString toConfigString(void) const = 0;
    virtual bool fromConfigString(const QStringList &config) = 0;

protected:
    quint8 i2cAddress;
};

Q_DECLARE_METATYPE(GCSensorI2C *)

typedef struct {
    quint8 repeatability;
    quint8 clockStretching;
    quint8 rate;
    quint8 periodicity;
} sensor_config_sht35_t;

class GCSensorSHT35 : public GCSensorI2C
{
public:
    enum Register
    {
        MEASUREMENT = 0x00,
        CONFIG = 0x01,
    };

    static constexpr uint8_t crcPolynomial = 0x31U;

    GCSensorSHT35(GCNode* const node = nullptr, quint8 interface_id=0, quint8 id = 0, quint8 i2cAddress = I2CAddressA);
    GCSensorSHT35(const GCSensorSHT35 &s) = default;
    ~GCSensorSHT35() override;

    static constexpr quint8 I2CAddressA = 0x44;
    static constexpr quint8 I2CAddressB = 0x45;
    static constexpr std::array<int, 2> i2cAddresses = {I2CAddressA, I2CAddressB};

    bool setI2CAddress(const quint8 a) override;
    bool setRepeatability(const quint8 a);
    bool setClockStretching(const quint8 a);
    bool setRate(const quint8 a);
    bool setPeriodicity(const quint8 a);

    const quint8 getRepeatability(void);
    const quint8 getClockStretching(void);
    const quint8 getRate(void);
    const quint8 getPeriodicity(void);

    int i2cAddressToInt(quint8 a) override;

    QString toString(void) const override;
    QString toConfigString(void) const override;
    bool fromConfigString(const QStringList &config) override;
    QList<GMessage> getConfigurationMessages() override;
    void saveData(std::vector<quint8>& data) override;
    void printHeader(void) override;

private:
    uint8_t calculateCrc(uint8_t b, uint8_t crc, uint8_t poly);

protected:
    sensor_config_sht35_t config;


};

Q_DECLARE_METATYPE(GCSensorSHT35 *)

class GCSensorAPDS9306 : public GCSensorI2C
{
public:
    enum Register {
        MEASUREMENT = 0x0,
        CONFIG = 0x1,
        TH_HIGH = 0x2,
        TH_LOW = 0x3,
    };

    GCSensorAPDS9306(GCNode* const node = nullptr, quint8 interface_id=0, quint8 id = 0, quint8 i2cAddress = 0x52);
    GCSensorAPDS9306(const GCSensorAPDS9306 &s) = default;
    ~GCSensorAPDS9306() override;

    bool setI2CAddress(const quint8 a) override;
    bool setAlsMeasurementRate(quint8);
    bool setAlsResolution(quint8);
    bool setAlsGain(quint8);
    bool setAlsIVCount(quint8);
    bool setAlsTHHigh(quint32);
    bool setAlsTHLow(quint32);

    quint8 getAlsMeasurementRate(void);
    quint8 getAlsResolution(void);
    quint8 getAlsGain(void);
    quint8 getAlsIVCount(void);
    quint32 getAlsTHHigh(void);
    quint32 getAlsTHLow(void);

    int i2cAddressToInt(quint8 a) override;

    QString toString(void) const override;
    QString toConfigString(void) const override;
    bool fromConfigString(const QStringList &config) override;
    QList<GMessage> getConfigurationMessages() override;
    void saveData(std::vector<quint8>& data) override;
    void printHeader(void) override;

private:
    quint8 alsMeasurementRate;
    quint8 alsResolution;
    quint8 alsGain;
    quint8 alsIVCount;

    quint32 alsTHHigh;
    quint32 alsTHLow;
};

Q_DECLARE_METATYPE(GCSensorAPDS9306 *)

class GCSensorADC12 : public GCSensor
{
public:
    enum Register
    {
        MEASUREMENT = 0x00,
        CONFIG = 0x01,
    };

    GCSensorADC12(GCNode* const node = nullptr, quint8 interface_id =0, quint8 id = 0);
    GCSensorADC12(const GCSensorADC12 &s) = default;
    ~GCSensorADC12() override;

    void setAverage(bool average);
    bool getAverage(void);

    QString toString(void) const override;
    QString toConfigString(void) const override;
    bool fromConfigString(const QStringList &config) override;
    QList<GMessage> getConfigurationMessages() override;
    void saveData(std::vector<quint8>& data) override;
    void printHeader(void) override;

protected:
    bool average;
};

Q_DECLARE_METATYPE(GCSensorADC12 *)


class GCSensorADC16 : public GCSensor
{
public:
    enum Register
    {
        MEASUREMENT = 0x00,
        CONFIG = 0x01,
        PGA = 0x02,
    };

    GCSensorADC16(GCNode* const node = nullptr, quint8 interface_id =0, quint8 id = 0);
    GCSensorADC16(const GCSensorADC16 &s) = default;
    ~GCSensorADC16() override;

    void setAverage(bool average);
    bool getAverage(void);

    void setGain(PGAGain gain);
    PGAGain getGain(void);

    void setAutoGain(bool autoGain);
    bool getAutoGain(void);

    QString toString(void) const override;
    QString toConfigString(void) const override;
    bool fromConfigString(const QStringList &config) override;
    QList<GMessage> getConfigurationMessages() override;
    void saveData(std::vector<quint8>& data) override;
    void printHeader(void) override;

protected:
    bool average;
    bool autoGainConfig;
    PGAGain gain;
};

Q_DECLARE_METATYPE(GCSensorADC16 *)

class GCSensorLIA : public GCSensor
{
public:
    enum Register
    {
        MEASUREMENT = 0x00,
        CONFIG = 0x01,
        PGA = 0x02,
    };

    enum Mode
    {
        F_50KHZ = 0x00,
        F_25KHZ = 0x01,
        F_10KHZ = 0x02,
        F_5KHZ  = 0x03,
        FS      = 0x04,
    };

    enum FrequencySetting
    {
        FREQ_10HZ  = 0,
        FREQ_20HZ  = 1,
        FREQ_50HZ  = 2,
        FREQ_100HZ = 3,
        FREQ_200HZ = 4,
        FREQ_500HZ = 5,
        FREQ_1KHZ  = 6,
        FREQ_2KHZ  = 7,
        FREQ_5KHZ  = 8,
        FREQ_10KHZ = 9,
        FREQ_20KHZ = 10,
        FREQ_50KHZ = 11,
    };


    GCSensorLIA(GCNode* const node = nullptr, quint8 interface_id =0, quint8 id = 0);
    GCSensorLIA(const GCSensorLIA &s) = default;
    ~GCSensorLIA() override;

    void setAutoGain(bool autoGain);
    bool getAutoGain(void);

    void setEnableOutput(bool output);
    bool getEnableOutput(void);

    void setGain(PGAGain gain);
    PGAGain getGain(void);

    QString toString(void) const override;
    QString toConfigString(void) const override;
    bool fromConfigString(const QStringList &config) override;
    QList<GMessage> getConfigurationMessages() override;
    void saveData(std::vector<quint8>& data) override;
    void printHeader(void) override;

protected:
    bool autoGainConfig;
    bool output;

    PGAGain gain;
    Mode mode;
    FrequencySetting fsHigh;
    FrequencySetting fsLow;

};

Q_DECLARE_METATYPE(GCSensorLIA *)

class GCSensorADS1219 : public GCSensorI2C
{
public:
    enum Register {
        MEASUREMENT = 0x0,
        CONFIG = 0x1,
        CHANNELS = 0x2,
    };

    enum ConversionMode {
        SingleShot = 0x00,
        Continuous = 0x01
    };

    enum ConversionRate {
        SPS_20 = 0x00,
        SPS_90 = 0x01,
        SPS_330 = 0x02,
        SPS_1000 = 0x03,
    };

    const std::vector<quint8> addressesOptions = {
        0b1000000,
        0b1000001,
        0b1000010,
        0b1000011,
        0b1000100,
        0b1000101,
        0b1000110,
        0b1000111,
        0b1001000,
        0b1001001,
        0b1001010,
        0b1001011,
        0b1001100,
        0b1001101,
        0b1001110,
        0b1001111};

    GCSensorADS1219(GCNode* const node = nullptr, quint8 interface_id=0, quint8 id = 0, quint8 i2cAddress = 0b1000000);
    GCSensorADS1219(const GCSensorADS1219 &s) = default;
    ~GCSensorADS1219() override;

    bool setI2CAddress(const quint8 a) override;
    bool setEnabledChannels(quint8);
    bool setGain(quint8);
    bool setConversionRate(quint8);
    bool setConversionMode(quint8);
    bool setReferenceVoltage(quint8);

    quint8 getEnabledChannels(void);
    quint8 getGain(void);
    quint8 getConversionRate(void);
    quint8 getConversionMode(void);
    quint8 getReferenceVoltage(void);

    int i2cAddressToInt(quint8 a) override;

    QString toString(void) const override;
    QString toConfigString(void) const override;
    bool fromConfigString(const QStringList &config) override;
    QList<GMessage> getConfigurationMessages() override;
    void saveData(std::vector<quint8>& data) override;
    void printHeader(void) override;

private:
    quint8 enabledChannels;
    quint8 gain;
    quint8 conversionRate;
    quint8 conversionMode;
    quint8 referenceVoltage;
};

Q_DECLARE_METATYPE(GCSensorADS1219 *)

#endif // GCSENSOR_H

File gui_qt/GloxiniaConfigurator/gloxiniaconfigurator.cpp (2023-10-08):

#include "gloxiniaconfigurator.h"
#include "./ui_gloxiniaconfigurator.h"
#include <QMessageBox>
#include <QStringList>
#include <QStringListModel>
#include <QAbstractItemView>
#include <gmessage.h>
#include <QSerialPortInfo>
#include <QInputDialog>
#include <sensorsht35dialog.h>
#include <QLineSeries>
#include <QDateTimeAxis>
#include <QChartView>
#include <QValueAxis>
#include <QFileDialog>
#include <QThread>
#include <QSettings>
#include <QStandardPaths>
#include <cfloat>
#include <QtGlobal>
#include <QRandomGenerator>

GloxiniaConfigurator::GloxiniaConfigurator(QWidget *parent)
    : QMainWindow(parent),
      ui(new Ui::GloxiniaConfigurator),
    status(new QLabel(this)),
    systemSettings(new SettingsDialog(this)),
    sensorSettings(new SensorDialog(this)),
    globalMeasurementPolicyDialog(new GlobalMeasurementPolicyDialog(this)),
      sensorAPDS9306_065Dialog(new SensorAPDS9306_065Dialog(this)),
      sensorSHT35Dialog(new SensorSHT35Dialog(this)),
      sensorADC12Dialog(new SensorADC12Dialog(this)),
      sensorADC16Dialog(new SensorADC16Dialog(this)),
      sensorLIADialog(new SensorLIADialog(this)),
      nodeDicioDialog(new NodeDicioDialog(this)),
      chart(new QChart),
      messageModel(new QStringListModel(this)),
      measurementSettings(new MeasurementSettingsDialog(this)),
      newProjectDialog(new NewProjectDialog(this)),
      updateDialog(new UpdateDialog(this)),
      liaEngineDialog(new LIAEngineDialog(this)),
      readoutDialog(new GCReadoutDialog(this)),
    sensorADS1219Dialog(new SensorADS1219Dialog(this))
{
    // build UI
    ui->setupUi(this);
    ui->statusbar->addWidget(status);

    mainLayout = new QHBoxLayout();
    // horizontal layout
    splitter = new QSplitter(this);
    splitter2 = new QSplitter(this);
    messageView = new QListView(this);
    systemOverview = new QTreeView(this);
    chartView = new QChartView(chart);

    mainLayout->addWidget(splitter);

    splitter->setOrientation(Qt::Horizontal);
    splitter->addWidget(systemOverview);
    splitter->addWidget(splitter2);

    splitter2->setOrientation(Qt::Vertical);
    splitter2->addWidget(messageView);
    splitter2->addWidget(chartView);

    chartView->setRenderHint(QPainter::Antialiasing);

    ui->centralwidget->setLayout(mainLayout);

    // auto update when points are removed/added
    //connect(series, &QXYSeries::pointAdded, this, &GloxiniaConfigurator::autoScaleChart);
    //seriesConnections.insert(0, connect(dummySeries, &QXYSeries::pointAdded, this, [this]{autoScaleSeries(dummySeries); }));

    this->treeModel = new TreeModel(this);

    // create recent files actions
    ui->menuFile->insertSeparator(ui->actionExit);
    QAction* pAction = ui->actionSave, *cAction;
    for(int i = 0; i < maxRecentFiles; i++)
    {
        cAction = new QAction(this);
        recentFileActions.append(cAction);
        ui->menuFile->insertAction(pAction, cAction);
    }
    recentFileSeparatorAction = ui->menuFile->insertSeparator(recentFileActions[0]);
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

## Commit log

2022-02-28 Started redesign of dicio for Gloxinia2
    [dicio.kicad_pcb, dicio.sch]
2022-04-15 Enclosure design.
    [part1.scad, part2.scad, part3.scad]
2022-04-15 New sylvatica design.
    [sylvatica.csv, sylvatica.kicad_pcb, sylvatica.kicad_sch, sylvatica.sch]
2022-04-15 New dicio design.
    [dicio.csv, dicio.kicad_pcb, dicio.kicad_sch, dicio.sch]
2022-04-15 Dicio design with PIC32 MCU
    [dicio.csv, dicio.kicad_pcb, dicio.kicad_sch, dicio.sch]
2022-04-15 New planalta design.
    [planalta.kicad_pcb, planalta.kicad_sch, planalta.sch]
2022-04-15 Top connector PCB
    [racemosa.kicad_pcb, racemosa.kicad_sch]
2022-04-15 Side connector PCB
    [reflexa.kicad_pcb, reflexa.kicad_sch]
2022-04-21 Updated enclosure based on first design run.
2022-04-21 Updated for new mounting hole locations
    [dicio.kicad_pcb, dicio.kicad_sch]
2022-04-21 Redesign for improved mounting hole placement.
    [racemosa.kicad_pcb, racemosa.kicad_sch]
2022-04-21 Partial redesign.
    [reflexa.kicad_pcb, reflexa.kicad_sch]
2022-09-01 New design
    [rupestris.kicad_pcb, rupestris.kicad_sch]
2022-09-01 Tool holes
2022-09-21 Improved design.
    [dicio.kicad_pcb, dicio.kicad_sch, dicio.sch]
2022-10-13 Various improvements to the enclusure design.
    [part1.scad, part3.scad, support_structure.scad]
2022-10-13 Prototype GUI update.
2022-10-13 Placement update.
    [dicio.kicad_pcb]
2022-11-03 Rename files and remove old one
    [case.scad, lid.scad, part3.scad]
2022-11-15 Remove PIC32 project.
    [dicio.csv, dicio.kicad_pcb, dicio.kicad_sch, dicio.sch]
2022-11-15 Updated files.
    [dicio.kicad_sch, racemosa.kicad_pcb, reflexa.kicad_pcb]
2022-11-24 SHT35 sensor can now be partially configured
2022-12-05 Remove debug prints.
2022-12-05 Add sensor config readout option.
2022-12-05 Simple node/sensor getter without using QModelIndex
2022-12-05 Sensor status updates are now handled correctly
2022-12-05 UART communication is now reliable
    - Enabled hardware flow control to prevent messages from disapearing.
    - Removed delays.
    - Added more powerful RX system in gloxinia where messages are
    processed in the main loop instead of during the interrupt.
2022-12-06 Added sensor stop command.
2022-12-06 Handle sensor data correctly.
2022-12-06 Add missing value to sensor_sht35_error_t.
2023-01-06 These documents should contain the documentation of the different connectors and hardware usage.
2023-01-06 Samtec connectors.
    [MMS-107-02-F-DV.stp, MMS-110-02-F-DV.stp, TMMH-105-01-T-DV.stp, TMMH-107-01-T-DV.stp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]
2023-01-06 New and updated board designs.
    [dicio-bcb.kicad_pcb, dicio-bcb.kicad_sch, dicio.kicad_pcb, dicio.kicad_sch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]
2023-01-09 Bug fixes
    Start measuring did not create a unique directory
    Sensor removal memory leak fixed
    Sensor removal puts empty data and does not remove interface
    Add sensor removed from context menu
2023-01-09 Gerber exports
    [dicio-bcb.kicad_pcb, dicio-bcb.kicad_sch, dicio.kicad_pcb, planalta.kicad_pcb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]
2023-01-12 Add stop sensor command.
2023-01-13 Add sensor plot functionality
2023-01-17 Bug fixes.
    Settings defined in preferences are now correctly served. Data duplication removed.
    Add plot and delete options are now disabled for empty sensor interfaces
2023-01-17 Optimisation to make sensor starts more logical
2023-01-17 Simplify sensor editing
2023-01-17 Add new processor for sensor config
2023-01-19 Expose RTCC pin for synchronisation
    [dicio-bcb.kicad_pcb, dicio-bcb.kicad_sch, dicio.kicad_pcb, dicio.kicad_sch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]
2023-01-19 Bug fixes for APDS9306
    Plot was not added
    File check when writing to unopened sensor (state mismatch)
2023-01-23 Bug fix in component layout
    Connector was not updated to latest version, resulting in mis alignment w.r.t. connector board.
    [sylvatica-tcb.kicad_pcb, sylvatica.kicad_pcb]
2023-01-31 Change some component sizes
    [dicio.kicad_pcb, dicio.kicad_sch]
2023-02-02 Removed depricated project
    [reflexa.kicad_pcb, reflexa.kicad_sch]
2023-02-24 Add ADC datasheet.
    [sylvatica.kicad_sch]
2023-04-17 Fix issue with labeling.
    [dicio.kicad_pcb, dicio.kicad_sch]
2023-04-17 Update pin config for new hardware
2023-04-25 Minor improvements.
    Mostly related to external pull-ups of 10k for I2C
    [planalta.kicad_pcb, planalta.kicad_sch, sylvatica.kicad_pcb, sylvatica.kicad_sch]
2023-05-05 Refactored code for more performant sensor config and added first versions of LIA en ADC16 sensors.
2023-05-09 Fix net issue.
    [sylvatica.kicad_pcb, sylvatica.kicad_sch]
2023-05-09 Finish rerouting VBUS/5V net
    [sylvatica.kicad_pcb]
2023-05-17 Add filtering structure for ADC12.
2023-05-23 Add sensor interfaces
2023-05-24 Reduced number of filter taps.
2023-06-07 Definitions of dicio ADC12 filtering.
2023-06-07 Set sensor ID correctly.
2023-06-07 Add new queue for print messages.
2023-06-16 Fix timer/threading bug.
2023-06-16 Update to new pin configuration.
2023-06-27 Move ADC16 hardware config outside of 16-bit analog sensor definition
2023-08-02 Various updates for Aisler order.
    [dicio-bcb.kicad_pcb, dicio-bcb.kicad_sch, dicio.kicad_pcb, dicio.kicad_sch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]
2023-08-02 New board for USB to header connector conversion.
    [usb-to-terminals.kicad_pcb, usb-to-terminals.kicad_sch]
2023-08-04 Add prototypes for new message types + rename other message
2023-08-04 New task interface + less debug prints.
2023-08-04 Disable debug prints.
2023-08-08 Add two new commands.
    Config loading/clearing from device memory.
    Also fixed some missing `emit`s.
2023-08-24 Set callback also in default case.
2023-09-05 Implement clock initialisation function. Add function to get current time as formatted struct.
2023-09-05 Correctly implement thread separation for serial
    The serial communcation is now properly separated into a new object and threading now works as expected.
    Some optimasation remains possible.
2023-09-21 Add new deactivate function to each sensor.
2023-09-21 Add new boards
    [hirsuta.kicad_pcb, hirsuta.kicad_sch, radiation_shield.scad, tantho.kicad_pcb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]
2023-09-25 Add new sensor: ADS1219.
2023-10-08 Bug fixes in ADS1219 sensor implementation.
2023-10-08 Add ADS1219 sensor implementation.

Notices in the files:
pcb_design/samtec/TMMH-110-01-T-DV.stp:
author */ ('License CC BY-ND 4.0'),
